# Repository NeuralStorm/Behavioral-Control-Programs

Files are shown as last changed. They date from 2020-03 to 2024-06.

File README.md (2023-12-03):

# Behavioral-Control-Programs

# Repo Layout

tilt_hardware_control/tilt_rewrite - tilt task control software  
tilt_hardware_control/tilt_docs - documentation for the tilt task hardware and software  
tilt_hardware_control/si_programmer_scripts - motor controller scripts for tilt task  
Primate_Joystick_Pull - NHP behavior task  
one_targ - center out task

## Related

schematics and board layouts for the voltage conversion board used with tilt_hardware_control are in the [hardware repo](https://github.com/NeuralStorm/hardware/tree/main/conversion_board)

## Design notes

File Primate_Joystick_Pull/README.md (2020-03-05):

# TempMonkeyImages
#EV01: Joystick 1 On
#EV02: Joystick 1 Off
#EV03: Joystick 2 On
#EV04: Joystick 2 Off
#EV05: Joystick 3 On
#EV06: Joystick 3 Off
#EV07: Joystick 4 On
#EV08: Joystick 4 Off
#EV09: Cineplex Home On
#EV10: Cineplex Home Off
#EV11: Cineplex Joystick On
#EV12: Cineplex Joystick Off
#EV19: Ready (Beginning of Trial)
#EV20: Correct Count (Time of Correct Tone)
#EV21: Incorrect Count (Time of Blooper Tone)
#EV23: Reward Count (Time of Reward)
#EV24: End of Trial
#EV25: DS 1
#EV26: GC 1
#EV27: DS 2
#EV28: GC 2
#EV29: DS 3
#EV30: GC 3
#EV31: DS 4 (Not Currently Used)
#EV32: GC 4 (Not Currently Used)

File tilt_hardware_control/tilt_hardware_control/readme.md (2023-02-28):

# Setup

Install dependencies  
`pip install -r requirements.txt`
`pip install -e ../../classifiers`

If using live graph view  
`pip install pyside6`  
if installation fails use  
`pip install pyside2==5.15.2`  

When using closed loop the plexon dll requires Visual C++ Redistributable for Visual Studio 2013  
https://www.microsoft.com/en-us/download/details.aspx?id=40784

# Usage

Example command line call
```bash
python main.py --config config.hjson
```

## Usage examples

Create a copy of `../tilt_docs/data_collection_template`.

`clock_source` will need to be changed to "internal" in `config.hjson` if running without the plexon system.

### Bias Collection

Run `run_bias.sh` in the data collection directory.

This will create a dated bias file.

### Open loop

Edit `config.hjson`; ensure `mode` is set to open_loop. Set `num_tilts` and `delay_range` to the desired values. `baseline`, `sham`, `reward` and `channels` can be ignored or removed from the config file.

Collect a bias file by running `run_bias.sh`.

Run `run_tilts.sh` in the data collection directory.  
This will read settings from `config.hjson` and create dated output files in the data collection directory.

The program will run through the specified number of tilts then wait for the user to press enter before exiting.

---
### Closed loop, initial run

Edit `config.hjson`; set `mode` to closed_loop, `baseline` to true and `sham` to false. Set `num_tilts`, `delay_range` and`reward` to the desired values.

Run `run_tilts.sh` in the data collection directory.  
This will read setting from `config.hjson` and create dated output files in the data collection directory.

The program will perform tilts and record the tilts and spikes.

---
### Closed loop, after initial run

Edit config used for the initial run and change `baseline` to false.  
Add `--template-in <file>` where `<file>` is the name of the template.json file created by the initial run.  
If a template file wasn't generated or different settings are needed a new template file can be generated using build_template.py.

Create or edit `labels.hjson`; set `channels` to the desired value. See [example_labels.hjson](./example_labels.hjson) for an example.

Run `run_tilts.sh` in the data collection directory.  
This will read settings from `config.hjson` and create dated output files in the data collection directory. Euclidian classifier templates are loaded from the specified template.json file.

The program will perform tilts and attempt to classify the tilt type based on the created templates and perform punish/reward actions based on if the classification was correct.

---
### Live view

Add the `--live` parameter to enable the live view.
```
python main.py --config config.hjson --monitor --live
```

### Calibrated live view

The path `/grf_python` will need to be substituted with the location of grf_python on your system ([Behavior-Analysis-Programs](https://github.com/moxon-lab-codebase/Behavior-Analysis-Programs), tested with commit `5f005e1a5530fd36f4ea0879e8453bc01a65871b`)

The environment variable `grf_python_path` must be set to the location of grf python.
e.g.  
`fish`
```
set -gx grf_python_path /grf_python
```
`bash`
```
export grf_python_path=/grf_python
```
`windows`
```
set grf_python_path=/grf_python
```

The python dependencies for grf_python will need to be installed.

Run the program
```
python main.py --config your_config.hjson --monitor --live-cal --live-bias ./your_bias_file
```

---
## Pausing

pressing enter will pause the program at the end of the current tilt. pressing enter will resume the program, pressing q then enter will exit the program

## Notes on clocks

Plexon outputs a 40khz clock signal. This is downsampled by a hardware downsampler to 1000hz and sent to Dev6/PFI6. Note that data collection must be started for the plexon system to output its 40khz clock.

Using plexon's clock signal instead of the internal nidaq clock means, given one known shared event (such as the start pulse), all the neural and grf data can be correlated in time. Without using a shared clock the two clocks will experience a different amount of drift and diverge over time.

clock_source should always be set to external in normal use.

## Strain guage reading recording

Strain guage data is recorded concurrently with the rest of the program.

Note: In some places the analysis pipeline refers to the side with two sensors as the hindlimbs but they could be the forelimbs if the animal is placed on the platform facing the other direction.  
With the forelimbs on a single sensor the sensor numbers correspond to the following limbs.  
sensor1: right hind limb  
sensor2: left hind limb  
sensor3: forelimbs

The output csv contains the following columns.

```
sensor1_s1
sensor1_s2
sensor1_s3
sensor1_s4
sensor1_s5
sensor1_s6
sensor2_s1
sensor2_s2
sensor2_s3
sensor2_s4
sensor2_s5
sensor2_s6
sensor3_s1
sensor3_s2
sensor3_s3
sensor3_s4
sensor3_s5
sensor3_s6
Strobe: signal that gos high when a tilt starts and low when it finishes
Start: ttl pulse indicating start of plexon recording
Inclinometer: Inclinometer
Timestamp: Timestamp (incremented by 1/sample rate for each row)
strobe_digital: digital version of Strobe passed through a schmidt trigger
tilt_midpoint: signal that gos high when the tilt reaches it's maximum inclination
stim: ttl pulse indicating stimulation was applied
```

# Program flow

The program has multiple modes, set with the `mode` config parameter. The behaviour of the different modes is listed below. Recording of analog data is handled the same way for all modes except bias (where live view can not be used). Stimulation works the same for all modes except bias and monitor where stimulation is not available.

## open_loop

```
create a list of tilt types
wait for start pulse
for i in 0..num_tilts:
    perform tilt i
    wait for after_tilt_delay
    if reward enabled:
        dispense water
    wait for a random time within delay_range
waits for the user to press enter
```

## closed_loop (baseline = true, yoked = false)

```
create a list of tilt types
wait for start pulse
for i in 0..num_tilts:
    clear pending plexon events
    start tilt i
    for event recieved from plexon within about 200ms:
        if event is a tilt:
            add event to classifier
        if event is a spike:
            add spike to classifier
    finish tilt
    wait for after_tilt_delay
    if reward enabled:
        dispense water
    wait for a random time within delay range
waits for the user to press enter
```

## closed_loop (baseline = false, yoked = false)

```
create a list of tilt types
for i in 0..num_tilts:
    clear pending plexon events
    start tilt i
    for event recieved from plexon within about 200ms:
        if event is a tilt:
            add event to classifier
        if event is a spike:
            add spike to classifier
    classify tilt
    if classification was correct:
        stop tilt and return to level
    if classification was incorrect:
        perform punish tilt
    finish tilt
    wait for after_tilt_delay
    if classification was correct and reward is enabled:
        dispense water
    wait for a random time within delay range
waits for the user to press enter
```

## closed_loop (baseline = false, yoked = true)

```
load list of tilt types from template
for i in 0..num_tilts:
    clear pending plexon events
    start tilt i
    wait about 200ms
    if recorded classification was correct:
        stop tilt and return to level
    if recorded classification was incorrect:
        perform punish tilt
    finish tilt
    wait for after_tilt_delay
    if recorded classification was correct and reward is enabled:
        dispense water
    wait for a random time within delay range
waits for the user to press enter
```

## stim

performs stimulation until enter is pressed

## monitor

waits for enter to be pressed (so recording/live view can be used without tilting)

## bias

records data for a fixed amount of time then exits

# Command line parameters

Some parameters aren't listed in the readme. Run the program with `--help` for a fill list of parameters.

`--config`  
path to hjson config file, see config parameters section

`--labels`  
path to labels config file, see label parameters section

`--bias`  
sets the mode to `bias`

`--overwrite`  
allows overwriting of existing output files

`--monitor`  
sets the mode to `monitor`

`--template-in`  
path to a template file created by a previous run of the program

required in closed loop non baseline, otherwise unused

`--template-out`  
automatically generate a template file at the specified path from the generated events and meta files before exiting

note: if there are a large number of spike events template generation could take a long time

`--loadcell-out`  
path to write ground reaction force data csv to

`--overwrite`  
overwrite exsting output files, if not specified the program will stop if the output file already exists

`--no-start-pulse`  
disable waiting for the plexon start pulse before performing tilts

`--live`  
show live graphs of analog recordings

# Config file

Config parameters that begin with `--` will be added to the passed command line parameters. Setting one of these paramaters to null will pass the command line parameter without a value following it.

The `-` parameter can be set to a list of strings which will be added to the command line parameters.

Other parameters are used as listed below.

## Config parameters

parameters marked with * are required in closed loop mode but do not need to be specified in other modes.  
parameters marked with ** are not required.  

`mode`: Literal['open_loop', 'closed_loop', 'monitor', 'bias']  
see program flow section

`clock_source`: Literal['external', 'internal']  
should normally be set to external

internal uses the internal nidaq clock. externel sets the clock to Dev6/PFI6

`clock_rate`: int  
The rate at which to collect samples in hertz.  
If clock_source is external this should typically be 1000.

`num_tilts`: int  
Number of tilts to perform. This number must be divisible by four. The tilts will be split evenly between the four tilt types.

`tilt_sequence`: Optional[List[str]]  
A fixed sequence of tilts to use instead of generating a randomized sequence. If specified `num_tilts` will be ignored. `sequence_repeat` and `sequence_shuffle` only apply if this parameter is specified.

`sequence_repeat`: int  
The number of times to repeat the tilt sequence.

`sequence_shuffle`: bool  
If true the tilt sequence is randomized. Applies before `sequence_repeat`.

`delay_range`: Tuple[float, float]  
Range of delays between trials in seconds.

`after_tilt_delay`: float  
Delay after tilt completion in seconds.

`baseline`*: Optional[bool]  
If false an input template will be used to classify tilts. If true spikes will be collected without performing classification.

`yoked`*: Optional[bool]  
If true the tilts from the input template will be repeated. If baseline is false the rewards and punish tilts will be repeated. `reward` must be true for rewards to be enabled.

`reward`: bool  
If true a water reward will be given after succesful decoding. If false no water reward will be given. If true the reward is always given with mode == open_loop or baseline == true.

`water_duration`: float  
Duration for which water is dispensed.

`plexon_lib`**: Optional[Literal['plex', 'opx']]  
'plex' uses the `pyplexclientts` library  
'opx' uses the `pyopxclient` library

'opx' should be used with newer plexon systems, 'plex' with older systems

defaults to 'opx'

`stim_enabled`: bool  

`stim_params`: Dict[str, Any]  

# Labels file

## Label parameters

`channels`: Dict[int, List[int]]  
Selects a set of plexon units to be used in the psth template. The parameters of the dict are plexon channels and the values are plexon units within that channel.

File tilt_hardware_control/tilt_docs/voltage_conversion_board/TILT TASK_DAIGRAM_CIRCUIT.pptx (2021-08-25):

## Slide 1

( Hardware Block diagram: Tilt system)

XS1/XS2 (Plexon Start)

TILT DAQ

Tilt type ( 8-bit Strobe-> DSP)

Plexon (MAP)

Spikes, evnts

Tilt type

Downsampler
clock

Motor Start (5)

TILT PC

1250 KHz clk

40KHz clk

Motor Start (24)

TTL conversion
cicrcuitry
(5<-> 24 V)

TILT SYSTEM
LOADCELL,
INCLINOMETER

PLEXON PC

SERVO DRIVE

Motor commands

Tilt type (5)

Spikes

(LFP, INC, ds clk)

SENSOR DATA

LOADCELL DAQ

Plexon (Breakout)

PREAMP

RAT

INC

LFP

For BMI:
Plexon PC can send Neural data to TILT PC via TCP/IP (PlexNet)

Tilt PC : Programs to send tilt events, BMI decoding, record load cell data

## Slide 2

NI-DAQ TO MOTOR

NOTE: YOU ALSO 2 MORE 5 TO 24 V CONVERTER , IF YOU HAVE TO PROVIDE BMI INTERRUPTS TO MOTOR

24V TO 5V (MOTOR START SIGNAL) START SIGNAL FROM MOTOR

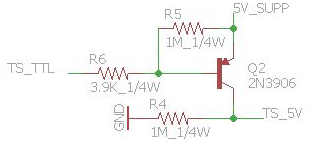
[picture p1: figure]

5 TO 12 V CONVERTER FOR WATER REWARD DELIVERY

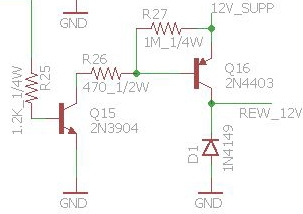
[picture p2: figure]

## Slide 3

Xcommon/ycommon/x7/x8-/x2-/x1- <->ground

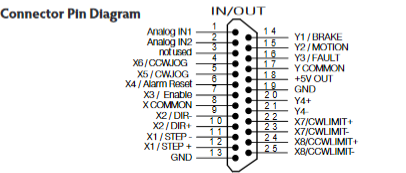
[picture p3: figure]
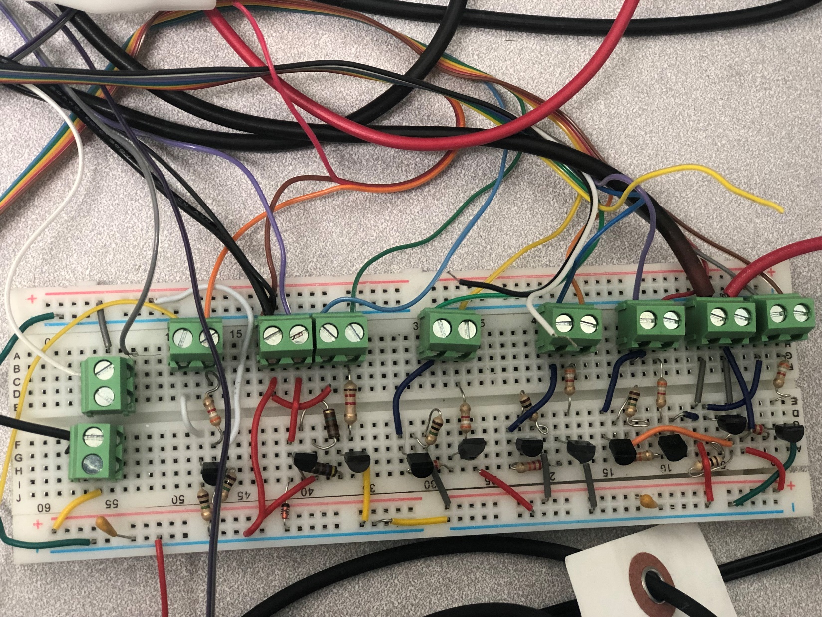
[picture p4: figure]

5 V SUPP

12V OUT PINCHER ( WATER)

GROUND

SMPS GROUND

GROUND

5 V LINE

24V SMPS SUPP

TTL_0 (IN->P0.0 NI6289 5V)

TTL_1 (IN->P0.01 NI6289 )

TTL_0 (O/P- MOTOR X3)

Y2 (MOTOR IN)

MOTOR OUT (TTL MOTOR START)

TTL_1 (O/P- MOTOR X4)

TTL_2 (IN->P0.2 NI6289 5V)

TTL_2 (O/P- MOTOR X5)

TTL_3 (IN->P0.3 NI6289 5V)

12 V LINE

TTL_3 (O/P- MOTOR X6)

12 V SUPP

WATER IN ( P0.4)

24V LINE

GROUND

GROUND

5 V INPUT FROM DAQ TO 24V OUTPUT (MOTOR)

24 TO 5V

5-12V WATER

X8+/x2+/ → bmi interrupt (punishment/reward)

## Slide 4

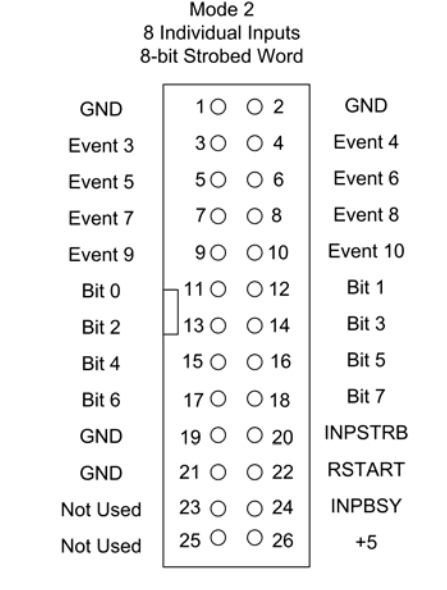
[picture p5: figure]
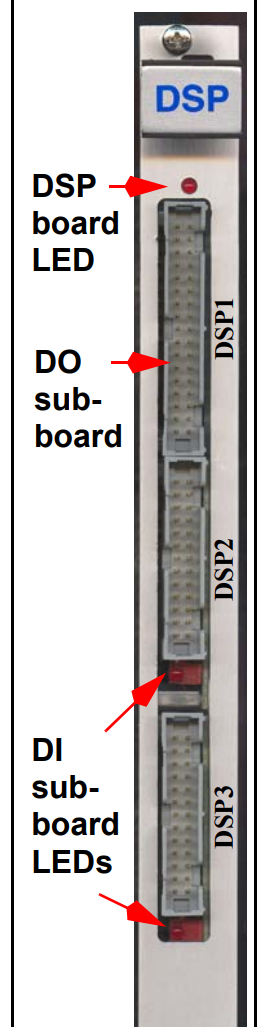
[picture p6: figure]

From TILT DAQ(USB 6289)

Motor start pulse

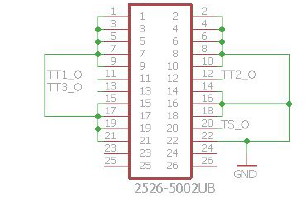
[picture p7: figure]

START PULSE FROM MAP ( XS1 TO NI DAQ 6289 P2.5)
INTERRUPT FOR BMI P1.2/P1.3 (USB 6289)

(MOTOR START)

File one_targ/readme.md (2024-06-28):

# Setup

copy `<project>/example_config.hjson` to `./config.hjson`

using python 3.11  
run `pip install .[hw]`

### Ubuntu 20 notes

To disable multi touch gestures in gnome the following extension can be installed.

https://extensions.gnome.org/extension/1140/disable-gestures/
```sh
gnome-extensions install disable-gestures@mattbell.com.au.v2.shell-extension.zip
gnome-extensions enable disable-gestures@mattbell.com.au
killall -3 gnome-shell
```

# Running

modify `./config.hjson` as needed

in bash
```sh
export nidaq=Dev3
export output_device=plexdo
one-targ
```

Press a to begin the task.

See comments in [example_config.hjson](./example_config.hjson) for descriptions of config parameters.

### Ubuntu 20 notes

If mouse input stops working after touch screen input `killall -3 gnome-shell` can resolve the issue.

# Hotkeys

\` (grave accent) - exit game  
`a` - start game  
`s` - stop game  
`f` - toggle fullscreen  
`c` - toggle calibration square (always 200x200 px)  

# Environment Variables

For environment variables marked [flag] any value that is set and not an empty string will enable the functionality.  
For example (bash)
```bash
export plexon=1
```

---
### `config_path`

use config file at path if no path is specified on the command line
default: `./config.hjson`

---
### `pos`

position the window with a specific location and size  
format {pos_x},{pos_y}<-{width}x{height}

this can be used to make the game effectively full screen

this changes how the game handles fullscreen and is likely required on ubuntu 20/gnome for correct functionality

example  
position at -1920,0
size 1920 by 1086
```sh
export pos='-1920,0<-1920x1086'
```

---
### `output_device`

juicer output device

`plexdo` - use plexon plexdo library  
`bridge` - use bridge  
`none` (default) - no output

---
### `nidaq`

nidaq device to use for event signal outputs. if not set nidaq output will be disabled

example
```sh
export nidaq=Dev3
```

---
### `bridge_enabled` [flag]

enables event output to the bridge server, enabled by default on linux  
if set to "`no`" bridge event output will be disabled

---
### `no_audio` [flag]

disables audio

---
### `photodiode_flash_duration`

photodiode marker flash duration in seconds, set to 0 to disable the photodiode marker flash  
default: 0.018

---
### `output_dir`

directory for output files  
default: `./output`

---
### `px_per_cm`

pixels per cm used to convert cm input values to pixels
default: 20.08

# misc dev notes

https://github.com/NeuralStorm/Behavioral-Control-Programs/tree/61a9baa6d198e3dc13d30326901ea78bd42dc77f/touchscreen_co/Touchscreen/One%20Targ

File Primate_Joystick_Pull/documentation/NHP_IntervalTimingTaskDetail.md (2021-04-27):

# Non-human Primate Interval Timing Task

## Homezone Exit task correct trial sequence

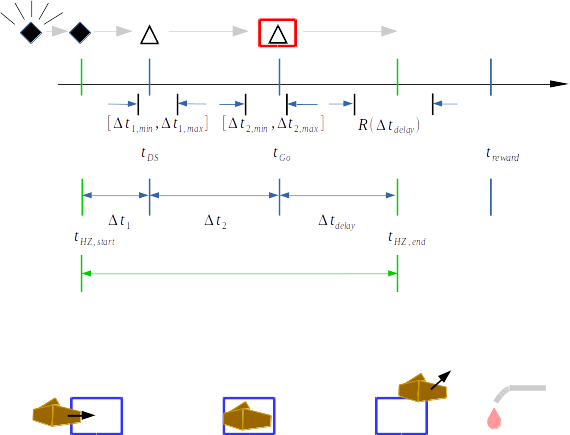
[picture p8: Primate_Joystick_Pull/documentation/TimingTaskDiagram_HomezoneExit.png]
NHP Homezone Exit task, correct trial sequence


Above: the series of animal-initiated events (green vertical markers), task-generated events  (blue vertical markers) and  measured intervals (horizontal arrows) during a correct trial of the homezone exit task.  The trial begins when on hand entry into the homezone target.  After a random interval of time between two user-specified limits $[\Delta t_{1, min}, \Delta t_{1, max}]$, a place-holder visual stimulus (triangle) is shown on the screen at $t_{DS}$.  The animal is cued to move its hand out of the homezone on appearance of a "Go" cue presented at $t_{Go}$; the Go cue takes the form of a red box that surrounds the discriminative stimulus already present on the screen.  If hand exit occurs within a user-specified limit a liquid reward is subsequently delivered, the volume of which scales as linearly-downward function dependent on $\Delta t_{delay}$.

Relevant parameters in `MonkeyImages_Joystick_Conf.py` as well as their corresponding key name and value(s) to load from configuration file, to setup "Homezone Exit" version of task:

- Version of task to run `TaskType`-> `Task Type`: `HomezoneExit` (ignored by program)
- Version of task to run `NumEvents`-> `Number of Events`: 0 (sets program to run homezone exit task)
- Graphics files directory path for task-specific visual stimuli: `source` -> `Path To Graphics Dir`: `"./TaskImages_HomezoneExit/"` (loads single triangle discriminative stimulus).
- ~~Number of unique intervals and relevant disciminative stimuli to setup in task: `NumEvents` -> `Number of Events`: `1`.~~
- `RewardClass(*Ranges)` -> `Ranges`: `1, 0.0, 3.0` (Function call to generate the single linear peak function for the sole discriminative stimulus (a triangle).  Description of each value in `Ranges` can be found in [Reward](#Reward) section below.)

## Joystick Pull Task correct trial sequence

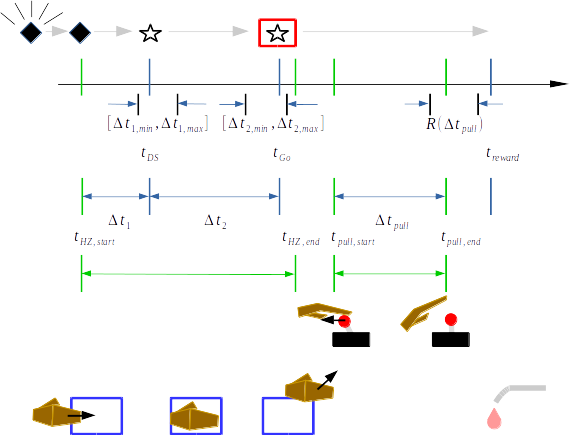
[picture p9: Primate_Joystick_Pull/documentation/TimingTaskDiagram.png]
NHP Joystick Pull task, correct trial sequence


Above: the series of animal-initiated events (green vertical markers), task-generated events  (blue vertical markers) and  measured intervals (horizontal arrows) during a correct trial of the interval timing task. After a random interval of time between two user-specified limits $[\Delta t_{1, min}, \Delta t_{1, max}]$, one of several possible discriminative stimuli is shown on the screen at $t_{DS}$; discriminative stimuli are geometric shapes that each code for a particular desired pull duration that the animal will be rewarded for producing later subsequently during the trial.  The animal is cued to start a joystick pull on the appearance of a "Go" cue presented at $t_{Go}$; the Go cue takes the form of a red box that surrounds the discriminative stimulus already present on the screen.  If the animal produces a joystick pull response of duration that falls within a user-specified time interval, a liquid reward is subsequently delivered, the volume of which scales as a bi-directional, linearly-dependent function of $\Delta t_{pull}$.

Relevant parameters in `MonkeyImages_Joystick_Conf.py` as well as their corresponding key name and value(s) to load from configuration file, to setup "Joystick" version of task:

- Version of task to run `TaskType`-> `Task Type`: `Joystick` (ignored by program)
- Graphics files directory path for task-specific visual stimuli: `source` -> `Path To Graphics Dir`: `"./TaskImages_Joystick/"` (loads three discriminative stimuli: oval, rectangle and star--one for each rewarded interval of the Joystick task.  More on this here [Visual Stimuli](#visual-stimuli)).
- Number of unique intervals and relevant disciminative stimuli to setup in task: `NumEvents` -> `Number of Events`: `3`. (sets the program to perform the joystick pull task)
- ~~`RewardClass(*Ranges)` -> `Ranges`: `3, 0.5, 0.25, 0.75, 0.5, 1.0, 0.75` (Function call to generate the three separate linear peak functions for the three discriminative stimuli in the joystick task.  Description of each value in `Ranges` can be found in [Reward configuration](#reward-configuration) section below.)~~
- `images` - see [the readme](../readme.md).
- `reward_thresholds` - see [the readme](../readme.md).

## Task Definitions (both versions)

### Negative Reinforcer type 1

When the animal's hand is outside of home-zone, a diamond shape flashes on screen at ~2Hz accompanied by and auditory ‘bell-dinging’ stimulus sounding repeating at ~0.5Hz.  These stimuli continue until animal’s hand enters home-zone.  This reinforcer is always present in both tasks; there is no boolean switch to turn it off.

Relevant parameters in `MonkeyImages_Joystick_Conf.py` as well as their corresponding key name and value(s) to load from configuration file:

- Graphics files directory link for visual stimuli -> `source` -> `Path To Graphics Dir`: `"./TaskImages_Joystick/"` or `"./TaskImages_HomezoneExit/"`.  Both contain the filled black diamond graphic that is to flash on the screen when the animal's hand is out of home zone.
- Audio file directory link (not included in config file) `OutOfHomeZoneSound` -> `'./TaskSounds/OutOfHomeZone.wav'`

### Task interval $\Delta t_1$ (task-generated)

The time interval spanning entry of hand into home-zone to appearance of the discriminative stimulus.  The duration of $\Delta t_1$ is randomly-drawn from a uniform distribution spanning $[\Delta t_{1,min}, \Delta t_{1,max}]$.  Animal must hold hand in home-zone for full duration of $\Delta t_1$ for the discriminative stimulus to appear.  If hand exits before the $\Delta t_1$ interval completes, the trial ends and the event is timestamped and recorded as a $t_1$-error.  Negative reinforcer type 1 immediately follows early exit occurrence to cue return of hand into home-zone if `EnablePullTimeOut == True`.

Relevant parameters in `MonkeyImages_Joystick_Conf.py` as well as their corresponding key name and value(s) to load from configuration file:

- $\Delta t_{1,min}$ -> `DiscrimStimMin` -> `Pre Discriminatory Stimulus Min delta t1`: `0.2` (seconds)
- $\Delta t_{1,max}$ -> `DiscrimStimMax` -> `Pre Discriminatory Stimulus Max delta t1`: `0.3` (seconds)
- $\Delta t_1$ -> `DiscrimStimDuration` -> Auto-generated in program from a uniform random draw in between limits above.

### Task interval $\Delta t_2$ (task-generated)

The time interval spanning appearance of the discriminative stimulus to appearance of the “Go” cue.  The duration of $\Delta t_2$ is randomly-drawn from a uniform distribution spanning $[\Delta t_{2,min}, \Delta t_{2,max}]$.  The "Go" cue is a red box that appears on screen that surrounds the (already present) discriminative stimulus.  The animal must continue to hold in home-zone for the full duration of $\Delta t_2$ for the Go cue to appear.  If animal's hand exits before interval completes, the trial ends and the event is timestamped and recorded as a $t_2$-error.  Negative reinforcer type 1 immediately follows early exit occurrence to cue return of hand into home-zone.

Relevant parameters in `MonkeyImages_Joystick_Conf.py` as well as their corresponding key name and value(s) to load from configuration file:

- $\Delta t_{2,min}$ -> `GoCueMin` -> `Pre Go Cue Min delta t2`: `0.45` (seconds)
- $\Delta t_{2,max}$ -> `GoCueMax` -> `Pre Go Cue Max delta t2`: `0.95` (seconds)
- $\Delta t_2$ -> `GoCueDuration` -> Auto-generated in program from a uniform random draw in between limits above.

### Negative reinforcer type 2

To follow post-go homezone exit events (Homezone Exit task) or pulls (Joystick task) of duration outside of the range associated with the discriminative stimulus.  Rewarded interval ranges are specified in `Ranges` parameter list as described in [Reward configuration](#reward-configuration).  In a negative reinforcement type 2 event, the screen goes dark for the duration `TimeOut`, with the option of an auditory "blooper" stimulus that sounds at the onset of the timeout period.

Relevant parameters in `MonkeyImages_Joystick_Conf.py`:

- `EarlyPullTimeOut` -> `Early Pull Time Out` : `FALSE` A Boolean switch for turning on/off occurrence of negative reinforcer type 2 to follow pull events that occur during either $\Delta t_1$ or $\Delta t_2$ intervals.  If `EarlyPullTimeOut` is set to `True`, the current trial ends on an early exit and negative reinforcer type 1 is presented.  If set to `False` the trial continues without interruption.
- `EnableTimeOut` -> `Enable Time Out`: `FALSE` A Boolean switch to enable type 2 negative reinforcement events to follow pull durations that are outside of rewarded range for the trial.
- `TimeOut` -> `Time Out`: `1.0` The duration of timeout intervals during type 2 negative reinforcement events in units of seconds.
- `EnableBlooperNoise` -> `Enable Blooper Noise`: `TRUE` A Boolean switch to specify if the "Blooper" sound should play at the start of type 2 timeout periods.
- `Bloop`: `'./TaskSounds/WrongHoldDuration.wav'` Audio file directory link (not included in config file) for blooper noise to be played on Negative Reinforcer type 2 events.

## Homezone Exit version trial sequence

After the appearance of the Go cue, the task monitors for disappearance of the hand marker from the home zone--a rectangular area in the top view of the reaching area of the rig as defined in Cineplex.  If disappearance does not occur within the time-ceiling of the rewarded interval as contained in `Ranges` ([Reward configuration](#reward-configuration) section), the trial ends, the lack of disappearance is recorded as a "no pull" event and the time of elapse is recorded after which a new trial begins following a time out period if enabed.  The time out occurs if `EnableTimeOut == True` that presents [negative reinforcement type 2](#negative-reinforcer-type-2).  If disappearance does occur (ideally in the form of removal of hand from home zone) within the time limit following Go cue appearance, the time of disappearance is measured as $\Delta t_{delay} = t_{HZ, end} - t_{Go}$ and a reward follows shortly thereafter.  The value of $\Delta t_{delay}$ determines the amount of fluid reward that is delivered to the animal as detailed in [Reward configuration](#reward-configuration).

Relevant parameters in `MonkeyImages_Joystick_Conf.py` as well as their corresponding key name and value(s) to load from configuration file:

- `NumEvents` -> `Number of Events`: `1`
- `RewardClass(*Ranges)` -> `Ranges`: `1, 0.0, 3.0` (seconds)
- `InterTrialTime` -> `Inter Trial Time`: `1.0` (seconds)
- `EnableTimeOut` -> `Enable Time Out`: `FALSE`
- `TimeOut` -> `Time Out`: `1.0` (seconds)
  
## Joystick Pull version trial sequence

Following Go cue presentation, task monitors for start of joystick pull.  If a pull does not occur within user specified amount of time (`MaxTimeAfterSound`) the trial ends, the absence of pull is recorded as a "no pull" event, the time of elapse is recorded and a new trial begins.  If pull occurs within time limit following Go cue appearance, the time of pull is measured as $\Delta t_{pull} = t_{pull,end} - t_{pull,start}$.  If $\Delta t_{pull}$ falls in the reward range associated with the particular discrimative stimulus on the screen, a fluid reward is delivered as described in [Reward configuration](#reward-configuration). If $\Delta t_{pull}$ is outside of the reward range for the trial, no reward is delivered, the trial ends, the times of the erroneous pull are recorded and classified as a "pull failure".  In the case of pull failure, if `EnableTimeOut == True`, then negative reinforcement type 2 is presented.  If `EnableTimeOut == False` the discriminative stimulus and Go cue remain on screen and the animal may attempt additional pulls for reward until the maximum time for the trial elapses (`MaxTimeAfterSound`).  Time-outs, if enabled, last for a duration specified by `TimeOut`  in units of seconds.  Successive trials are separated by an intertrial time of `InterTrialTime` in units of seconds.

Relevant parameters in `MonkeyImages_Joystick_Conf.py` as well as their corresponding key name and value(s) to load from configuration file:

- `MaxTimeAfterSound` -> `Maximum Time After Sound`: `20.0` (seconds)
- `InterTrialTime` -> `Inter Trial Time`: `1.0` (seconds)
- `EnableTimeOut` -> `Enable Time Out`: `FALSE`
- `TimeOut` -> `Time Out`: `1.0` (seconds)
  
## Reward configuration (outdated)

see `reward_thresholds` in [the readme](../readme.md) for updated information

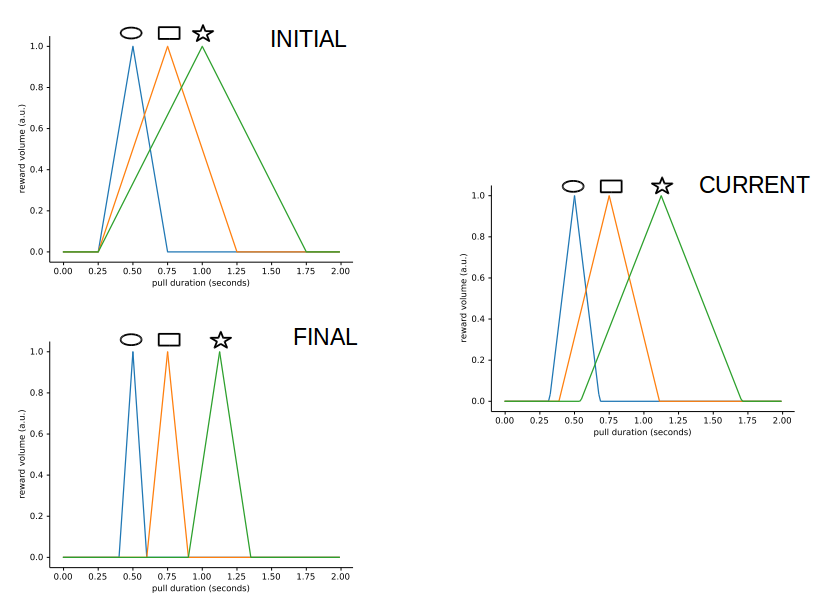
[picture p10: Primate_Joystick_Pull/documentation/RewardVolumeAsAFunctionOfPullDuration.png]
Reward volume as a function of $\Delta t_{pull}$


Functional relationship, depicted graphically, of fluid reward volume dependence on pull duration, $R(\Delta t_{pull})$, for each discriminative stimulus of joystick task.  Shown above each associated function peak is the corresponding Discriminative Stimulus (oval, rectangle and star) that is used to inform the desired pull duration for a given trial.  A triangle DS would appear over a single peak function for the case of the Homezone Exit version (not shown).  Peak values of functions are located at the desired pull duration (for the associated DS) for which a pull response elicits maximal reward.  Reward volume drops-off linearly the further away pull response duration departs from desired (location of peak) on a given trial.  Top Left: Reward function shapes at initial stage of training: the interval floors of disciminative stimulus-associated ranges are set at 0.25 seconds and functions have substantial overlap.  Bottom Left: End goal of reward functions after response shaping: DS-associated functions do not overlap.  Middle right: Current settings of DS-associated reward functions.

Relevant parameters in `MonkeyImages_Joystick_Conf.py` as well as their corresponding key name and value(s) to load from configuration file:

- `NumEvents` -> `Number of Events`: `1` or `3` (for Homezone Exit and Joystick tasks respectively)The number of disciminative stimulus-associated intervals to include in the task.
- `RewardClass(*Ranges)`: Method that generates each associated linear peak function for each discriminative stimulus to be included in the task.  In the argument list `Ranges`, the first in the list must be an integer number of intervals to include in the task.  This first argument is assigned to attribute `NumEvents` in the code.  Each group of two floats that follow in the `Ranges` list define the respective peak location $t_{peak}$, and peak width at base $\Delta t_{width}$ for each interval to be included.  Resulting peak function ($t_{floor} = t_{peak} - \Delta t_{width}$) and high boundary with respect to peak ($t_{ceiling} = t_{peak} + \Delta t_{width}$) for the associated interval.  That is, `RewardClass(*Ranges)` are of the form `Ranges` = $[N_{events}, t_{peak, 1},  \Delta t_{width,1}, ..., t_{peak, i}, \Delta t_{width, i}, ..., t_{peak, N}, \Delta t_{width, N}]$.  Examples: `RewardClass(3, 0.5, 0.25, 0.75, 0.5, 1, 0.75)` for Joystick task and `RewardClass(1, 0.0, 3.0)` for Homezone Exit version.
- `Ranges` is the key name in the configuration file that idetified the list of interval definition values (described above) that are read into the `RewardClass(*Ranges)` method.
- `MaxReward` -> `Maximum Reward Time`: `0.18` (seconds). Specifies the maxiumum time, in units of seconds, for which the feeder is advanced for all intervals--it corresponds to the peak height of each reward function.
- `RewardDelayMin` -> `Pre Reward Delay Min delta t3`: 0.5 (seconds).  Minimum length of delay before fluid reward delivery following completion of a successful trial.
- `RewardDelayMax` -> `Pre Reward Delay Max delta t3`: 0.5 (seconds).  Maximum length of delay before fluid reward delivery following completion of a successful trial.
- `RewardDelay = RandomDuration(RewardDelayMin, RewardDelayMax)`:  Method that draws actual length of delay separating reward delivery from trial completion on a particular trial.
- `UseMaximumRewardTime` -> `Use Maximum Reward Time`: `FALSE`.  Boolean toggle to override duration-dependent reward delivery $R(\Delta t_{pull})$ or $R(\Delta t_{delay})$. Instead, task simply delivers fixed-volume rewards of size `MaxReward` regardless of response accuracy.

Finally it is essential to note that each interval defined in `RewardClass(*Ranges)` must have corresponding graphics files of the associated discriminative stimulus and Go cue in the graphics file directory specified in the configuration file.  See [Visual stimuli configuration](#visual-stimuli-configuration).

## Visual stimuli configuration

In `MonkeyImages_Joystick_Conf.py` all visual stimuli are graphical files in Portable Network Graphic (.png) format.  Stimuli include the "enter homezone" cue (solid diamond), each of the discriminative stimuli (oval, rectangle and star shaped outlines) for the "Joystick" task and (triangle) for the "Homezone Exit" task as well as their corresponding images to cue reach (oval in red box, rectangle in red box and star in red box) and (triangle in red box)--the red box surrounding a DS is the "cue to start pull" or "Go" cue.  Stimuli also include the black blank screen presented during [Negative Reinforcement Events of Type 2](#negative-reinforcer-type-2).

Relevant parameters in `MonkeyImages_Joystick_Conf.py` as well as their corresponding key name and value(s) to load from configuration file:

- `source` -> `Path To Graphics Dir`: `"./TaskImages_HomezoneExit/"`or `"./TaskImages_Joystick/"`.  Path to folder containing all graphical image stimuli to be displayed during the course of a trial.  Files must be named alphabetically in order of their appearance in the trial sequence.
- `ChooseReward()` : Method to select, at random from a uniform distribution, the particular interval to be rewarded for the given trial, as well as the associated discriminative stimulus to present for the selected interval during the trial sequence.

## Task sounds configuration

Parameters to define auditory stimuli and cues given during task sequences for both "Joystick" and "Homezone Exit" versions of `MonkeyImages_Joystick_Conf.py`.  Relevant attributes and example values are as follows:

- `RewardSound = 'Exclamation'`.  Winsound used to indication successful completion of trial.
- `Bloop = str(Path('./TaskSounds/WrongHoldDuration.wav'))`.  Path to wav file of a "blooper" noise that is sounded (if enabled) at the onset of Negative Reinforcement type 2 event.
- `OutOfHomeZoneSound = str(Path('./TaskSounds/OutOfHomeZone.wav'))`.  Path to wav file of a "bell dinging" that is repetitively sounded at during Negative Reinforcement type 1 event (that signals for animal to return hand to home zone).
  
NOTE: The above parameter definitions are NOT included in the configuration file.  Alterations to sound file path parameters must be made to the code itself.

## Joystick channel selection (currently not implemented)

- `ActiveJoystickChans` -> `Active Joystick Channels`: `3`  Comma-separated list of channels to include for control of the Joystick Pull version of the task.  Value `3` corresponds to the "pull" direction of joystick (toward animal).  Channel `1` is the "push" direction (away from animal) and channels `2` and `4` are in directions of animal's left and right respectively.

## Unused (untested?) configuration options

These were included in early version of task development.  Not sure if functionality of these options has been tested.  Descriptions here are taken directly from comments in code.

- `ImageRatio`: `100` Example: ImageRatio = 75 => 75% Image Reward, 25% Water Reward , Currently does not handle the both choice for water and image. (Not included in configuration file)
- `WaterReward = self.WaterRewardThread()`: ??? (Not included in configuration file)
- `AdaptiveValue` -> `Adaptive Value`: Probably going to use this in the form of a value
- `AdaptiveAlgorithm` -> `Adaptive Algorithm`: 1: Percentage based change 2: mean, std, calculated shift of distribution (Don't move center?) 3: TBD Move center as well?
- `AdaptiveFrequency` -> `Adaptive Frequency`: Number of trials in-between calling `AdaptiveRewardThreshold()`

## Metadata and output filename generation

Meta data values record the who, what, when and why of a particular task session and include the values in the task output file for later classification.  Object attribute in code and corresponding key name in task configuration file are as follows:

- `StudyID` -> `Study ID` : 3 letter study code for the current task session (example value: `TIP`),
- `SessionID` -> `Session ID`:  Session type identifier code.
- `AnimalID` -> `Animal ID`: 3 digit animal identification number (example value: `001`).
- `Date` is auto-generated by the program at start up.
- `TaskType` -> `Task Type`:  (example values: `Joystick` or `HomezoneExit`)

When saving task events and performance statistics to an output csv file at the end of the session, the default filename for which is auto-generated as follows:

- `filename = StudyID + '_' + AnimalID + '_' + Date + '_' + TaskType + '.csv'`.
- Example: `TIP_001_20200715_HomezoneExit.csv`.

The file is saved to the destination path specified in the configuration file under the key:

- `savepath` -> `'Task Data Save Dir'` with the paired example value  `D:\IntervalTimingTaskData`.

## Task output

Pressing the "Save CSV" button on the task GUI during run-time generates a text file of task performance data in comma-separate value format.  The following list describes each field contained therein:

### Session level statistics

- `Total Trials`:  Total number of trials performed both successes and failures
- `Total t1 failures`:  Number of trials during which hand exited prior to DS-appearance
- `Total t2 failures`:  Number of trials during which hand exited prior to Go cue appearance
- `Total pull failures`:  Number of trials that animal pulled for a duration OUTSIDE of rewarded interval for the associated DS presented on a given trial.
- `No Pull`:  Number of trials for which the animal made no pull response after appearance of Go cue.
- `Total successes`:  Number of trials for which the animal made a pull response of duration within the rewarded interval for the associated DS presented on a given trial.
- `Check Trials`: `True` or `False`.  (I do not know what this field means...)
- `Paw into Home Box: Start`: For a given trial (indicated by column position) timestamp of hand entry into homezone.  Units of seconds since start of task.
- `Paw out of Home Box: End`  For a given trial (indicated by column position) timestamp of hand exit from homezone.  If trial outcome is a "no pull" then the end-of-trial timestamp is reported instead.  Units of seconds since start of task.
- `Discriminant Stimuli On`: For a given trial (indicated by column position) timestamp of first appearance of disciminative stimulus on the screen.   Units of seconds since start of task.
- `Go Cue On`: For a given trial (indicated by column position) timestamp of first appearance of Go cue on the screen.  Units of seconds since start of task.
- `Trial DS Type`: Identification number of desired pull duration interval and associated discriminative stimulus for the given trial.  ID number corresponds with order of intervals as they are listed in `Ranges` (in groups of two after the first argument) in the configuration file.  A value of `0` is reported if the trial ends in a $t_{1}$-error.
- `Duration in Home Zone`: Duration of time that hand is in homezone (seconds)--Calculated as `Paw out of Home Box: End` minus `Paw into Home Box: Start`.
- `Trial Outcome`: String-valued classification of trial outcome.  Possible values: (`'t1-Fail'`, - `'t2-Fail'`, `'Pull Fail'`, `'Success'`, `'No Pull'`).
- `Trial End`: Timestamp of trial completion regardless of outcome.  Units of seconds since start of task.
- `Post t1 failure pull counter`:  Number of pulls made by animal following occurence of $t_{1}$-error prior to start of next trial.
- `Post t2 failure pull counter`:  Number of pulls made by animal following occurence of $t_{2}$-error prior to start of next trial.

NOTE: For output files generated from HomezoneExit task sessions, hand exit events are listed as "pulls".

### Interval/DS-specific level statistics

- `Discriminatory Stimulus Trial Count #`: Number of intervals/DSs of type # during the session.
- `Correct Stim Count #`: Number of trials with success outcome for interval/DS type # subset.
- `Incorrect Stim Count #`: Number of trials with a fail outcome for interval/DS type # subset.
- `Correct Average #`: Average of correct response measure for interval/DS type # subset: $\bar{\Delta t_{pull}}$ for Joystick version and $\bar{\Delta t_{delay}}$ for Homezone Exit version.
- `Correct St Dev #`: Standard deviation of correct response measure for interval/DS type # subset.

### Interval/DS-specific event timestamps and durations

Timestamp of appearance or corresponding duration for each trial of interval/DS type # subset.  If event did not occur for trial due to error event, place-holder `------>` is inserted in cell that timestamp or duration would otherwise occupy.  One column per trial over course of the task session.

- `Discriminatory Stimulus #`
- `Go Cue #`
- `Correct Start Press #`
- `Correct End Press #`
- `Correct Duration #`
- `Reward Duration #`
- `Incorrect Start Press #`
- `Incorrect End Press #`
- `Incorrect Duration #`

## Task startup sequence

1. Turn power switch to "on" in back of OmniPlex Chassis
2. Turn on recording computer.
3. Start OmniPlex Server.  Configuration file 'TIP_Basic_2.pxs' should autoload.  Warning message appears; press OK.
4. Turn on PlexControl.  Load configuration 'TIP_Basic_NOSPK.pxc'.
5. Start Data Monitoring Mode ("Play" triangle icon in menu bar).
6. Check joystick real time output to verify proper connectivity.
7. Start CinePlex.  Load most recent (or desired) settings file.
8. Modify applicable configuration file (if necessary) in `C:\PythonSDK_python3\ConfigFiles`.
9. Start Anaconda Prompt.  Navigate to code directory `cd C:\PlexonSDK_python3\Behavioral-Control-Programs\Primate_Joystick_Pull`.
10. At the terminal command prompt, start virtual environment (python version 3.7, 32-bit) by typing `conda activate py37_32`.
11. Run the program by typing `python MonkeyImages_Joystick_Conf.py` at the command  prompt.  This should start the program and ask user to navigate and select applicable configuration file.
12. Select configuration file.  The terminal should next prompt user to start recording the PlexControl .plx file. Take this pause as an opportunity to arm CinePlex video recording if desired.
13. Start recording in PlexControl by pressing red triangular "play" icon.  A menu should appear asking for the save path and file name of the plx file to be written.  Enter in appropriate file name and destination path in navigator window.
14. The task window should now appear.  Drag window to rig monitor leaving "Start" button visible on the Plexon monitor screen for easy access.
15. Press "Start" button on task window to start task.
16. End task by pressing the "Stop" button on task window GUI.
17. Save task performance data by pressing "Save CSV" button on the task GUI.  Be sure to check terminal for successful save or a prompt to enter a unique filename.  The program should not save over file with same name unless instructed by user.
18. Remember to  end Plexon recording as well by pressing the square "stop" icon in top icon ribbon of PlexControl.

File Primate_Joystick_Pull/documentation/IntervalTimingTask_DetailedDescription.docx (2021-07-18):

Moxon NHP Lab – Joystick Task

Updated April 27, 2021 KM

The documents provides an overview of the training procedure for the joystick task and how the task is intended to progress. The goal of the training is to have the animals pull and hold a joystick for a specific temporal intervals depending on a cue.

Overview and Logistics

Training Phases

  1. Transporting
  2. Cage side joystick – encourage to hold for long time
  3. Painting hand
  4. Chair Training
  5. Head Restraints
  6. Hand in Home-Zone
  7. Go Cue
  8. Hold for Long duration
  9. Add second cue for shorter duration
  10. Add a third cue for additional duration
  11. Add a fourth cue

After monkeys have been chair trained and allow painting on their hand they will be trained to perform the Joystick task. In parallel, they are also being acclimated to head-restraining pads Task training will take place at least once per day, last no longer than 4 hours, Monday through Friday, in TB-144, room SS2016 of the CNPRC. Training is broken down into 9 Phases:

During training, the animal will be positioned in the chair and yoked with or without his head restrained, with the joystick within reaching distance of his extended forelimb. A reach-blocking plate on the chair will be used to permit reaching from either the monkey’s left or right side. The distance of the joystick from the chair will be positioned will be adjusted to accommodate different reach lengths of different monkeys. Monkeys may be trained to perform the task using limbs on either (or both) their left and/or right sides. Because neurons in motor cortex have been well documented to modulate their activation levels depending on the direction of reach (directional tuning) the animal will be required to start the task from a consistent (across trials) home position. Because motor preparation is also of interest, the animal will be required to wait for a go cue before initiating the joystick pull.

To guide the task, distinct auditory and visual cues will be presented. Visual cues are presented on flat-screen monitor within the monkey’s visual field. Auditory cues are played over speakers.

Definitions

Trial – a trial begins when the animal puts its paw in the home position. A trial ends when the animal either gets a reward or makes an incorrect response as defined below

Home position – the placement of the paw at the start of the trial where the marker on the animal’s paw is in the home zone

Home zone – a region defined by the Plexon video software. The software can monitor when the paw is in the home position by monitoring whether the marker on the back of the hand is in the home zone.

Task Parameters – parameters in blue are generated by the program, parameters in black are give by the user in the config file.

thome – the amount of time the animal must keep its paw in the home position for that trial. This number is a random variable, calculated by the program, selected from a uniform distribution between tmin and tmax

tmin – the minimal time the user wants the animal to keep its paw in the home position

tmax - the maximum time the user wants the animal to keep its paw in the home position

Δtlow Δthigh the precision with which the animal must hold his hand in home zone on each trial given by the user. For the Interval Cue Presentation step (see below) the animal must keep its paw in the home zone for at least thome - Δtlow. For the Reach Production step (see below) the animal must remove its paw from the home zone within thome + Δthigh

thpactual – the length of time the animal kept its paw in the home position, determined by the program

for intervals

number of intervals – the number of temporal intervals the program selects from to present as cues for the animal. Currently the number of intervals can be to 1, 2 or 3 to allow 1, 2 or 3 intervals. Or the number of intervals can be set to 0 and the program ends, giving the monkey a reward if he keeps his paw in the home position for thome

tpullmax and tpullmin – user defined minimums and maximums, define by the user for each interval, that the defines the range within which the monkey has to pull the joystick for a reward

e.g. tpullmin1 tpullmax1 tpullmin2 tpullmax2 tpullmin3 tpullmax3

tpull – the actual length of time the monkey pulled the joystick for – the joystick was in the activated state

trelease – the amount of time the program waits after the animal releases the joystick before a reward is delivered

Task progression

1. The monkey must have the marker on his responding hand positioned within the home zone to start a trial. This defines the start of a trial.

When a trial starts, the program randomly selects the cue from the user’s list of possible cues and calculates thome

2. Interval Cue presentation: Presentation of the interval occurs at the beginning of each trial as soon as the animal puts its paw in the home position. The particular cue presented (e.g. shape on the screen) indicates the duration of the joystick pull that will be rewarded.
3. Go cue: Animal must learn to hold its paw in the home position for the required period of time, from thome - Δtlow to thome + Δthigh. A correct response at this stage of the task is hand in home position the minimal amount of time thome - thome - Δtlow). An incorrect response at this stage is when the animal removes his hand from the home position early
  a. Correct Reponses -> program place a red circle around the interval cue (go cue) and continues to next step
  b. Incorrect response -> trial ends, blooper tone sounds, screen goes blank until monkey puts paw back into home position and then a new trial starts. Trial data are written to a file (trial number, tmin, tmax , thome, Δtlow Δthigh thpactual )
4. Reach production: The monkey must move its paw out of the home position within thome + Δthigh for a correct response. If the monkey leaves it paw in the home position for more than thome + Δthigh then it is an incorrect response
  a. Correct Reponses -> program continues to next step
  b. Incorrect response -> trial ends, blooper tone sounds, screen goes blank until monkey puts paw back into home position and then a new trial starts. Trial data are written to a file (trial number, tmin, tmax , thome, Δtlow Δthigh thpactual )

NOTE: if the number of intervals = 0, the program ends here. For a correct response the animal gets its reward and trial data are written to a file (trial number, tmin, tmax , thome, Δtlow Δthigh thpactual )

5. Interval production: The monkey must pull the joystick to the “on” position, keeping the mechanism in the activated state continuously for the cued duration. The cued duration is defined by the user as an interval between a max and min value, one set for each cue. An auditory tone sounds when the joystick is in on position (Hold Tone). On release, one of two cases will occur:
  a. Correct Response: The monkey releases the joystick within the specified time window about the target time between tmin and tmax for that interval. Program continues.
  b. Incorrect response: The monkey releases the button outside of the specified time window between tmin and tmax for the seleted interval. Trial ends, blooper tone sound, screen goes blank until monkey puts paw back into home zone and then new trial starts. Trial data are written to a file (trial number, tmin, tmax , thome, Δtlow Δthigh thpactual, interval number (1,2,or 3), tmin for that interval, tmax for that interval and tpull for the trial.)
6. Reward Event: An auditory tone sounds and a reward is delivered based on the pull interval (see below) trelease after the joystick is released. The trial is labelled a success, the trial ends and trial data are written to a file (trial number, tmin, tmax , thome, Δtlow Δthigh thpactual, interval number (1,2,or 3), tpullmin for that interval, tpullmax for that interval and tpull for the trial.)

Variants of this task are described in Knudsen,…,Moxon, J. Neurosci. 2014 and Zarco,…,Merchant J. Neurophys. 2009. Wang, …, Jazayeri, Nature Neuroscience

2018.

Auditory Stimuli

We plan to incorporate auditory stimuli into the to facilitate task acquisition and guide attention. Two or three distinct auditory stimuli--each comprised of a distinct pitch or timbre--would be generated from a nearby speaker at an intensity no louder than 80 decibels to signal:

1. During-hold: when the button or lever is in the activated (e.g. depressed or pulled) state.

2. Successful trial completion

3. Reward delivery

Visual Stimuli

A unique stimulus (computer graphics that can vary in terms of number shape and/or color) will code for each interval duration that a monkey must produce on a given trial to receive a reward. We plan on training at most six distinct interval-duration ranges, with corresponding visual stimuli, with values between 0.2 to 6 seconds.

Task acquisition

To train monkeys on the task, we will first gradually and imperceptibly increase the required duration that a monkey must keep paw in home zone to receive a reward. Once this is working well (what does ‘well’ mean). The reach to pull joystick for durations part of task will start.

Second, we will gradually increase the duration in order to receive reward until the max pull duration is achieved. Initially, the stimulus associated with the longest duration will be shown on the screen in front of the animal. Once the monkey regularly produces intervals of maximum duration (6 seconds), shorter duration trials, and their associated stimuli, will be introduced in a randomized sequence along with the long duration trials. Task acquisition will be evaluated statistically: that is, when an interval produced for the presented cue occurs at a frequency significantly greater than chance. If an animal reaches a max pull duration >2s but less than 6, a decision will be made to move on to a second duration.

Reward scaling

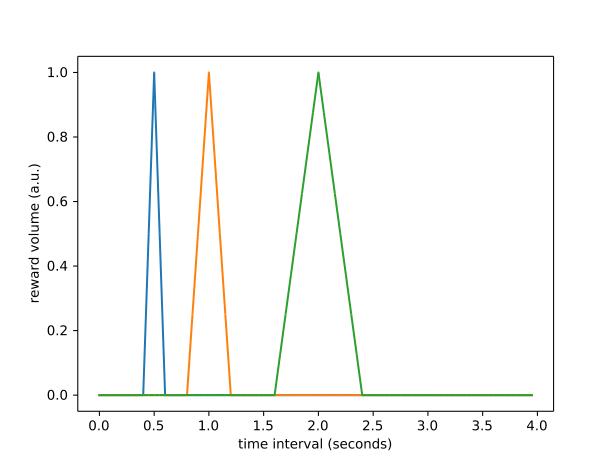
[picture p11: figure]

Figure 1: Reward volume as a function of produced interval. Target intervals in this example are located at the center of each peak at 0.5, 1.0 and 2.0 seconds. Widths of peaks increase linearly with duration of target interval.

Because production of long intervals requires more effort and attention than short intervals, we could have monkeys receive greater reward (e.g. greater volume of applesauce) for successful completion of long intervals. Volume of sauce reward will scale with duration of the produced interval. This follows methods described in Zarco, …, Merchant J. Neurophys 2009.

Alternatively, amount of reward could also be delivered as a multi-peak function emphasizing interval precision; that is, with each peak located at the location of each target interval to be produced and with peaks about longer target intervals having greater width. See figure 1. below illustrating hypothetical reward volume as a function of produced interval according to this paradigm. A similar reward paradigm is described in Wang, …, Jazayeri, Nature Neuroscience 2018.

Weber’s Law

We expect variability of timed interval responses from monkeys to observe Weber’s law: standard deviation of the distribution of produced intervals is directly proportional to the average duration of those intervals. Therefore, rewarded ranges about long target intervals will be set comparatively wider than rewarded ranges for shorter target intervals (e.g. if the range of rewarded intervals about target interval t = 0.5 is [0.4, 0.6], the rewarded range about target interval t = 1.5 might be [1.25, 1.75]).

Performance shaping – this did not work well for us

~~Once task acquisition has been demonstrated, press durations will be further shaped by gradually and imperceptibly reducing the range of durations that are rewarded about the target duration. For example, for a desired press duration of t = 2 seconds, the range of rewarded press durations on these trials will be gradually reduced from between 1 to 3 seconds to 1.5 to 2.5 seconds. Range limits will be adjusted in increments of +or-~~ ~~0.05~~ ~~sec for every~~ ~~100~~ ~~trials completed.~~

~~To maximize the number of presses made by monkeys during training, and subsequent testing, the ratio of number of correct presses to number of rewards will be gradually and imperceptibly increased under a variable reinforcement schedule. Specifically, the reward ratio will be increased by~~ ~~0.01~~ ~~for every~~ ~~200~~ ~~correct trials completed, starting at 1:1 until the reaching a possible maximum of~~ ~~6:1~~~~. The end goal of SPHT training is for a monkey to perform a series of presses, ranging between~~ ~~0.2 to 6~~ ~~seconds for no less than~~ ~~200~~ ~~trials per session.~~

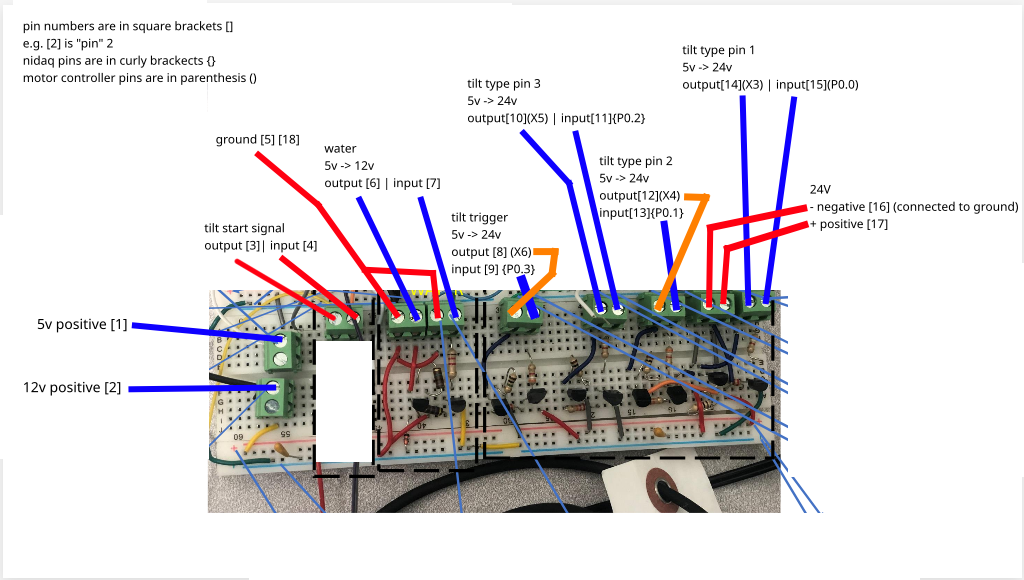
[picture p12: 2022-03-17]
tilt_hardware_control/tilt_docs/voltage_conversion_board/voltage_conversion_board_pinout.png

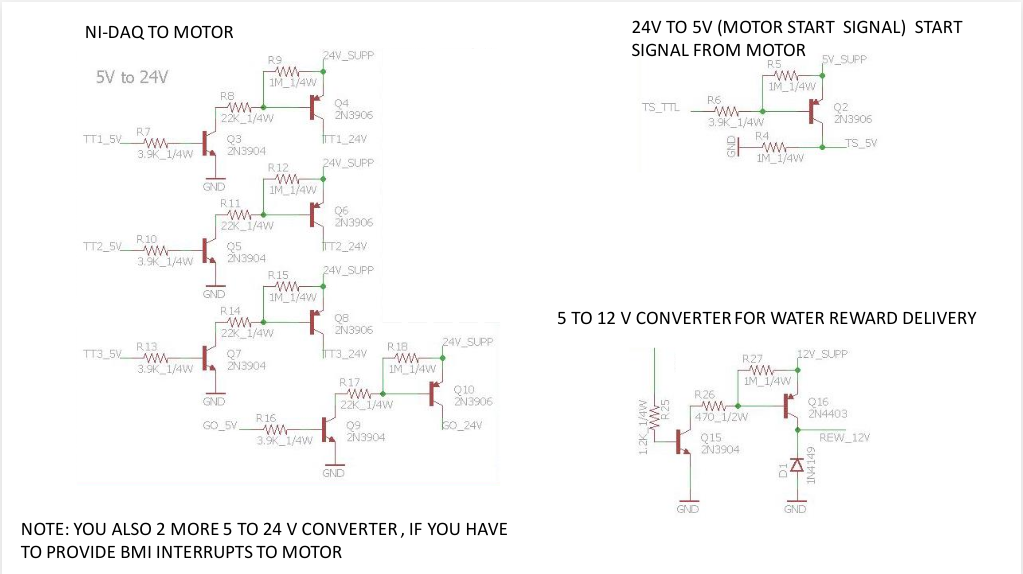
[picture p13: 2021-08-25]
tilt_hardware_control/tilt_docs/voltage_conversion_board/shot_20210824_215824.png

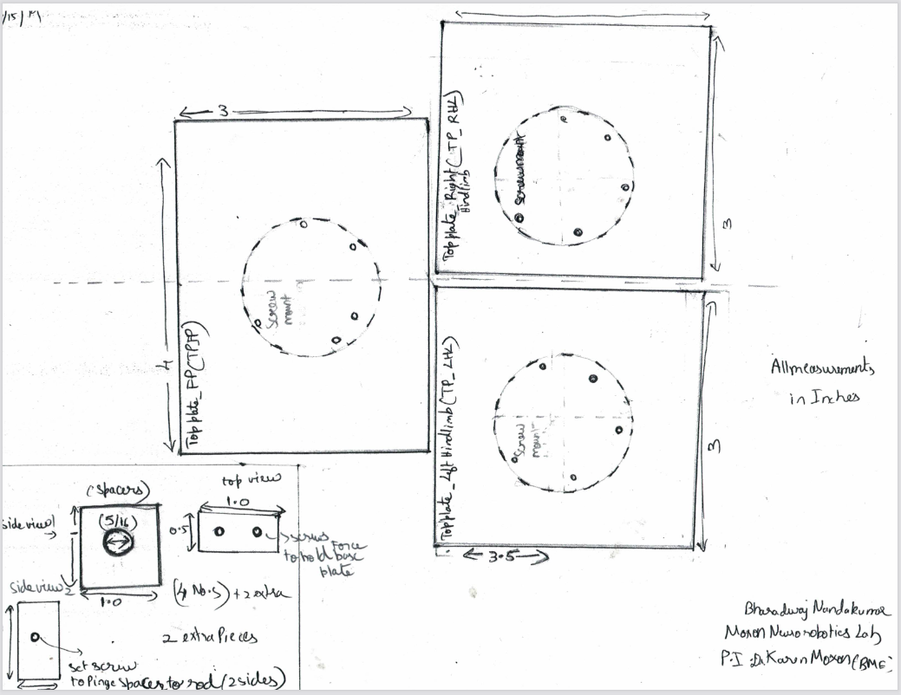
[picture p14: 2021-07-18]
tilt_hardware_control/tilt_docs/platform_drawing_top.png

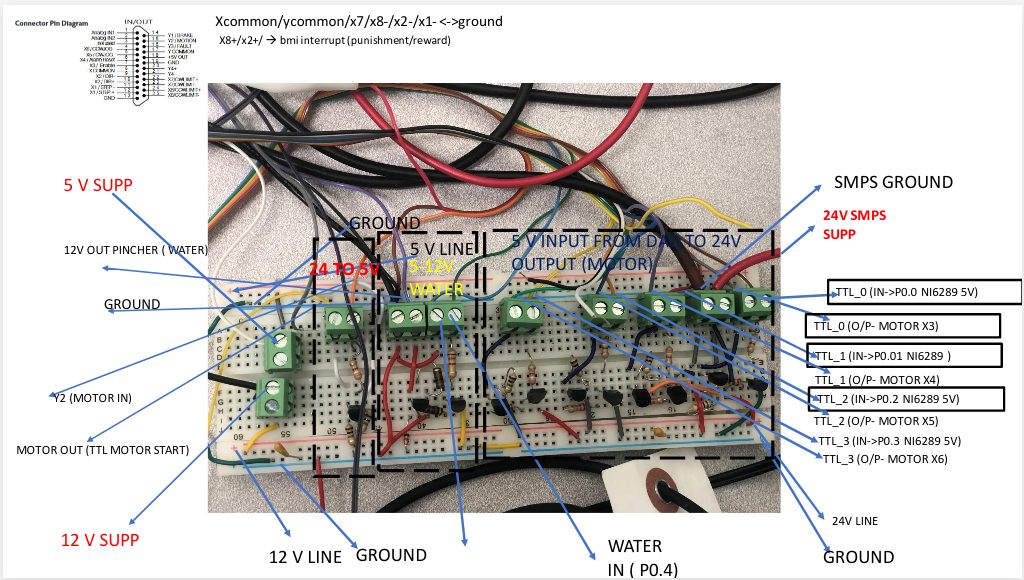
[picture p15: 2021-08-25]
tilt_hardware_control/tilt_docs/voltage_conversion_board/shot_20210824_215838.png

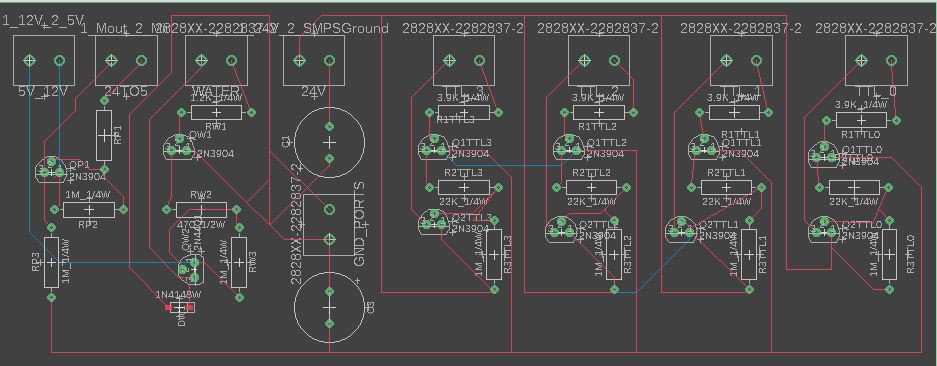
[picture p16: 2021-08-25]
tilt_hardware_control/tilt_docs/voltage_conversion_board/CircuitImage.JPG

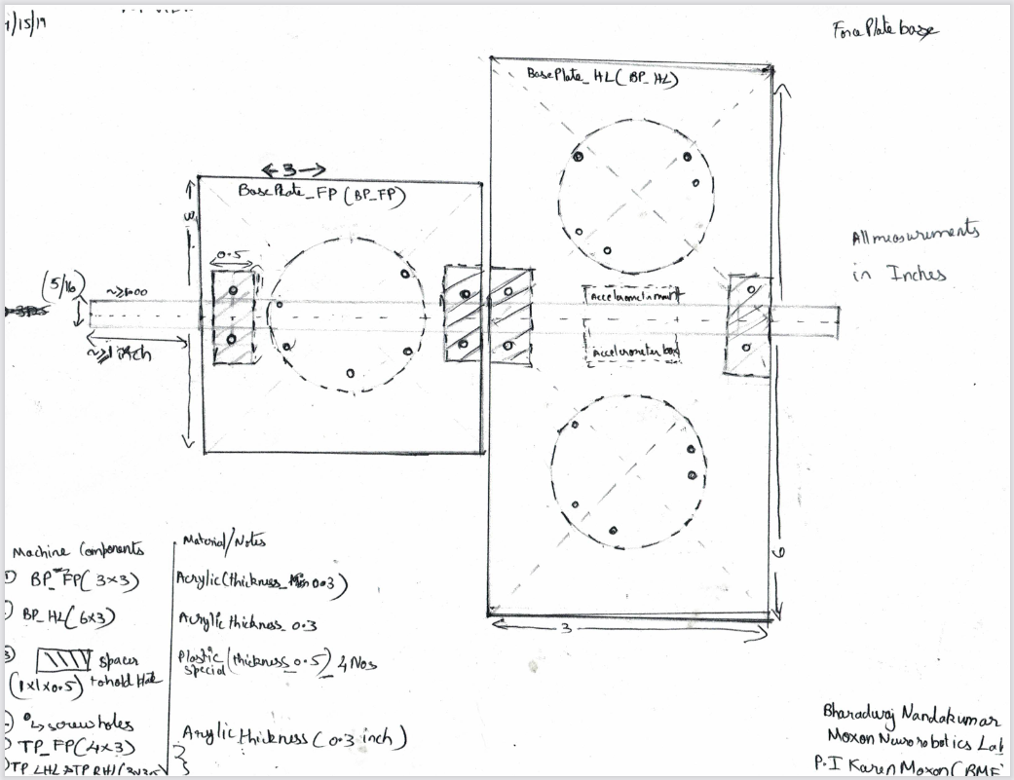
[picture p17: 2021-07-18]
tilt_hardware_control/tilt_docs/platform_drawing_bottom.png

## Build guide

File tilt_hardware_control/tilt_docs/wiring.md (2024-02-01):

for devices besides the voltage conversion board the pinouts can be found in the manual for the given device. note that for the for the USB pinout information is in the SCB-68 quick reference for the SCSI version

the force/toque sensors connect to the nidaq directly via a scsi connector. the SCB-68 breakout board is daisy chained through the sensor amplifier  
"CONNECTOR 0" on the nidaq connects to "Connector 0 to DAQ Card" on the amplifier  
"CONNECTOR 1" on the nidaq connects to "Connector 1 to DAQ Card" on the amplifier  
"Connector 1 from User" connects to the SCB-68 breakout board

## devices

pin numbers are prefixed based on the device/port, e.g. tim(5) is pin 5 on the plexon timing board

---
`downsample` - clock downsampling board

port numbers correspond to the labels on the downsampling board

---
`nidaq` - SCB-68 breakout board on conenctor 0 of the NI 6225 nidaq connected to the tilt computer

port numbers will have both the number labeled on the breakout board and the pin's name  
e.g. `nidaq(P0.0|52)` is pin P0.0 and labeled 52 on the SCB-68 breakout board

in cases where pins have multiple functions only the relevent one will be written, e.g. `PFI 6 / P1.6` will be listed as `PFI 6`

---
`motor` - SV7-Si motor controller IN/OUT1

port numbers will have both the port number and part or all of the name, e.g. `motor(Y2|15)` is port 15 which has the name "Y2 / MOTION"

the SI software refers to pins Y1-Y4 as output 1-4, X1-X4 as input 1-4. these terms may be used interchangably in some places

---
`tim` - plexon TIM board d-sub connector

port numbers will have both the port number and the name, e.g. `tim(40 kHz|5)` is port 5 which is named "40 kHz"

---
`din` - plexon DIN board port B

port numbers will have both the port number and part or all of the name, e.g. `din(Data 1|17)` is port 1 which has the name "Data 17"

---
---

## ground
the following pins should all be connected together

`nidaq(AI GND|67)`  
`nidaq(D GND|12)`  
`conv(5)`  
`conv(18)` (optional)  
`conv(16)` (optional)  
`downsample(Pwr -)`  
`downsample(In -)`  
`downsample(out -)`  
`din(Ground|19)`  
`tim(GND|15)`

## power
the nidaq, plexon, f/t sensor amp and motor controller have external power sources that need to be connected

`downsample(Pwr +)` - `nidaq(+5V|8)`

## tilt type to plexon

`nidaq(P2.2)` - `din(Data 22|6)`  
`nidaq(P2.3)` - `din(Data 25|9)`  
`nidaq(P2.4)` - `din(Data 21|5)`  
`nidaq(P2.5)` - `din(Data 24|8)`

## tilt timing for recording

`nidaq(P2.0)` - `nidaq(P0.0)`  
`nidaq(P2.1)` - `nidaq(P0.1)`

## inclinometer

the inclinometer should be connected to `nidaq(AI 10|31)`

## plexon clock

`tim(40 kHz|5)` - `downsample(In +)`  
`downsample(out +)` - `nidaq(PFI 6|5)`

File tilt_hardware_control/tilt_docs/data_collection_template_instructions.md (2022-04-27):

create a copy of the `data_collection_template` directory, the copy should go somewhere outside the `tilt_hardware_control` directory  
the template directory can be found in the tilt_docs directory which is pinned to Quick Access

modify `config.hjson`

`.sh` files can be run in git bash by double clicking them

`run_tilts.sh` performs tilts and collects data from the grf sensors, displays the live graphs  
`run_bias.sh` collects a bias file  
`run_monitor.sh` displays the live graphs and collects data without tilting

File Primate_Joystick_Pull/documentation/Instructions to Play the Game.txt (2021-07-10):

Start Omniplex server
Open PlexControl – load config file (be sure the system is stopped – black square with green line)

Open Cineplex – load config file joystick task.txt
Arm the video – hit the white A in the red circle

Go to:
C:\PlexonSDK_python3\Behavioral-Control-Programs\Primate_Joystick_Pull
Right click in Explorer – select ‘Gitbash Here’
In the command window type:
winpty py MonkeyImages_Joystick_Conf.py
Opens file selection dialogue.Open file:
 C:\PlexonSDK_python3\Behavioral-Control-Programs\Primate_Joystick_Pull\csvconfig_EXAMPLE_Joystick.csv
Start Plexon Recording (hit the start record icon)
 Select a file to write data to

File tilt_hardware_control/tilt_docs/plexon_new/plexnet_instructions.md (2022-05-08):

plexon: 128.120.197.198
tilt  : 128.120.197.189

Below my email signature, I've included some information for getting PlexNet set up. When you refer to the below ideas (in the steps below my email signature), please note that the “PlexNetLocal.exe”, “PlexNetRemote.exe”, and “PlexClient.dll” all come bundled with the installation of the specific version of the OmniPlex software which the customer is using. These files can be found at “C-->Program Files (x86) -->Plexon Inc-->OmniPlex”. Please be sure to use these specific versions of these files when considering the below ideas.

Quick Start for PlexNet:

1) Start OmniPlex and begin data acquisition normally.
2) Run PlexNetLocal.exe
3) Write down the IP address shown in PlexNetLocal.
4) Copy PlexNetRemote.exe and PlexClient.dll to the remote PC.
5) On the remote PC, run PlexNetRemote.exe.
6) In PlexNetRemote, click “PlexNet Server Address and Port.”
7) Enter the IP address that you wrote down in step 3 (from PlexNetLocal).
8) Click OK.
9) Click “Connect.”
10)You should see messages indicating that PlexNetRemote is connected and that data is being received.
a. The MMF bar populating/updating indicates that data’s flowing. Also, a non-zero “kb/s” value indicates that data is flowing.
11) At this point, you can run an online client on the remote machine, which will receive data just as if it were running on the same PC as OmniPlex.  
a. In PlexNetRemote, the “Data Transfer Options” allow you to configure things like which continuous channels are sent over PlexNet. Most clients don’t need things like the wideband continuous data, so by default those channels are not sent over PlexNet. Note that you have to click “Connect” before PlexNetRemote will let you see the Data Transfer Options.  
If you’re interested in WB and/or SPKC data getting to PlexNet Remote, you also have to go to OmniPlex Server and do these steps:
    1. Stop Data acquisition.
    2. Click Online Client Options. [ConfigureOnline Client Options]
    3. Set the sampling rate to 40,000 Hz. (default is 1000).
    4. Make sure “Enable Online Client access…” is checked.
12) When you are done running clients on the remote machine, click Disconnect in PlexNetRemote.

After this first-time setup, just perform steps 1,2,5,9 to start, and 11,12 to shut down. You don’t need to re-enter the IP address in PlexNetRemote, unless the IP address of the local PC changes. To keep things simple, on the remote machine place PlexNetRemote.exe and PlexClient.dll in the same folder as your client programs. This avoids issues with the client not being able to find PlexClient.dll, or finding the wrong version.

Some settings that should generally not need to be changed:
If for some reason the default of port 6000 is not acceptable, for example, the network administrator has blocked or reserved it, find out what port number is available and enter that value in both PlexNetLocal and PlexNetRemote.

Leave the protocol set to the default of TCP/IP in both Local and Remote. Only change this setting to UDP if the remote machine does not support TCP/IP, which is rare.

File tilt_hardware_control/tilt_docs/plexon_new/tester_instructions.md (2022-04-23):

parts:  
* the blue rectangular piece called the DI Status indicator
* the small green piece called the DI Generator

# Usage

For your testing, please go into the OmniPlex Server software and set Port A to “Event Word” Mode and set Port B to “Individual Events” mode. Please set the logic to High True for both ports for the testing. Chapter 10 of the OmniPlex User Guide https://plexon.com/wp-content/uploads/2020/01/OmniPlex-User-Guide.pdf provides useful information for setting up this configuration.

The first thing you can try is simply plugging in the DI Status indicator piece (the blue rectangular piece) first into Port A, and then next into Port B. When you do this, is every light on the DI Status Indicator illuminating in each case? This would be expected behavior if so. If this does not happen, please let us know. The behavior for LEDs “A”, “B”, and “C” is not strictly defined,  so if you see different behavior for those three LEDs specifically, that is not problematic.

After verifying the above, then next please plug the DI Status Indicator piece back into Port A. Then, plug the DI Generator (the small green item) into the other end of the DI Status Indicator. When the DI Generator is plugged in, it receives power from the Digital Input card, and this causes the DI Generator to generate a pattern of digital signals. When the DI Generator is plugged to the Digital Input card, it repeats the following pattern:

It raises bit 0, then raises and lowers the STROBE bit, then it lowers bit 0. For each of the remaining output bits (1 to 15), the generator continues this pattern. It raises the bit, raises and lowers the STROBE bit, and then lowers the bit. Finally, after bit 15 has been lowered, the DI generator raises and lowers the RSTART bit.

When  you run through this process with the DI Generator plugged into Port A (Event Word mode), the raising of the STROBE bit generates a strobed event in OmniPlex. The strobed event has a value associated with it corresponding to the setting of the individual bits at the time the STROBE was raised. Sine the DI generator raises one bit at a time, 16 strobed event values are generated (1,2,4,8…32768).

When you run through this process with the DI Generator plugged into Port B (Individual Events mode), the raising of a single bit generates a corresponding event in PlexControl software. Bit 0 creates an event 1 (EVT17 since port B corresponds to EVT17-EVT32), bit 1 creates EVT18, etc. In this mode, raising the STROBE bit does not generate any events.

In either of the test modes mentioned above, the rising of the RSTART bit generates an RSTART event and the lowering of the RSTART bit creates an RSTOP event. Note however that only Port A on the Digital Input card generates RSTART and RSTOP events.

If you’d like you can make one short (~10-20 second) PL2 file recording for each of the Ports using the above testing set-up described for each port, and you can send us these short recordings, so that we can look at the recordings in the NeuroExplorer software.

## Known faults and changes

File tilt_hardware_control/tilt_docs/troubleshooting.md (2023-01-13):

# Common errors

`daqmx.errors.DaqError: Some or all of the samples requested have not yet been acquired.`

This is typically caused by plexon data acquisition not being started. The plexon system only generates the needed clock signal while data acquisition is running.

If neural data is not being collected the clock source can be switched to internal.

---

`daqmx.errors.DaqError: The specified resource is reserved. The operation could not be completed as specified.`

Ensure no other instances of the tilt control program is running, including in monitor mode. If this doesn't work the python processes may need to be killed with task manager.

The device can be made available by resseting it in NI Max but this can leave left over processes that can still interact with other shared resources so it is likely better to restart the computer.

This can also be resolved by restarting the computer.

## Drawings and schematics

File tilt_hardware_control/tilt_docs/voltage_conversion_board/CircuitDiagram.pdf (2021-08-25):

# 2N3904 GND

# 2 TTL_0

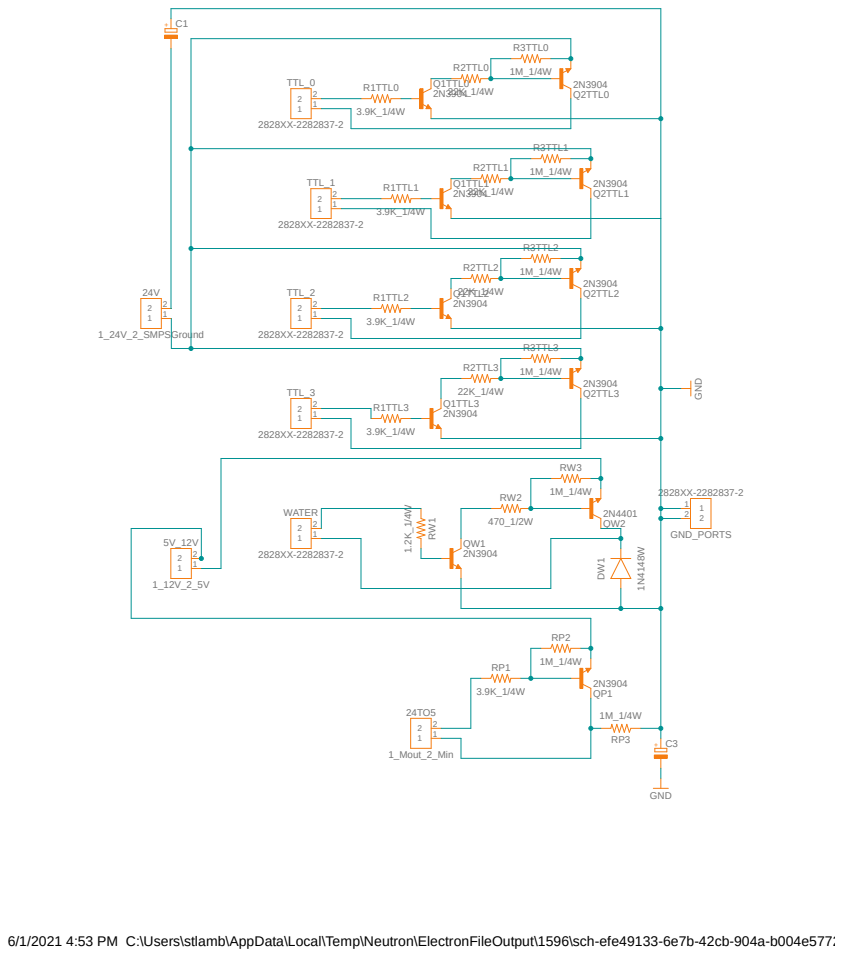
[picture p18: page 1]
GND ¹.2K_1/4W; 1_Mout_2_Min; 2 RW¹; QW2 DW¹; 1N⁴¹⁴⁸W; R1TTL3; R2TTL3; R3TTL3; Q1TTL3; Q2TTL3; R1TTL2; R2TTL2; R3TTL2; Q1TTL2; Q2TTL2; R1TTL1; R2TTL1; R3TTL1; Q1TTL1; Q2TTL1; R1TTL0; R2TTL0; R3TTL0; Q1TTL0; Q2TTL0; TTL_3; 2 TTL_2; 2TTL_1; 1_24V_2_SMPSGround; 2 WATER; 2 GND_PORTS

6/1/2021 4:53 PM C:\Users\stlamb\AppData\Local\Temp\Neutron\ElectronFileOutput\1596\sch-efe49133-6e7b-42cb-904a-b004e5772f45\MoxonCircuitBoard v7.sch (Sheet: 1/1)

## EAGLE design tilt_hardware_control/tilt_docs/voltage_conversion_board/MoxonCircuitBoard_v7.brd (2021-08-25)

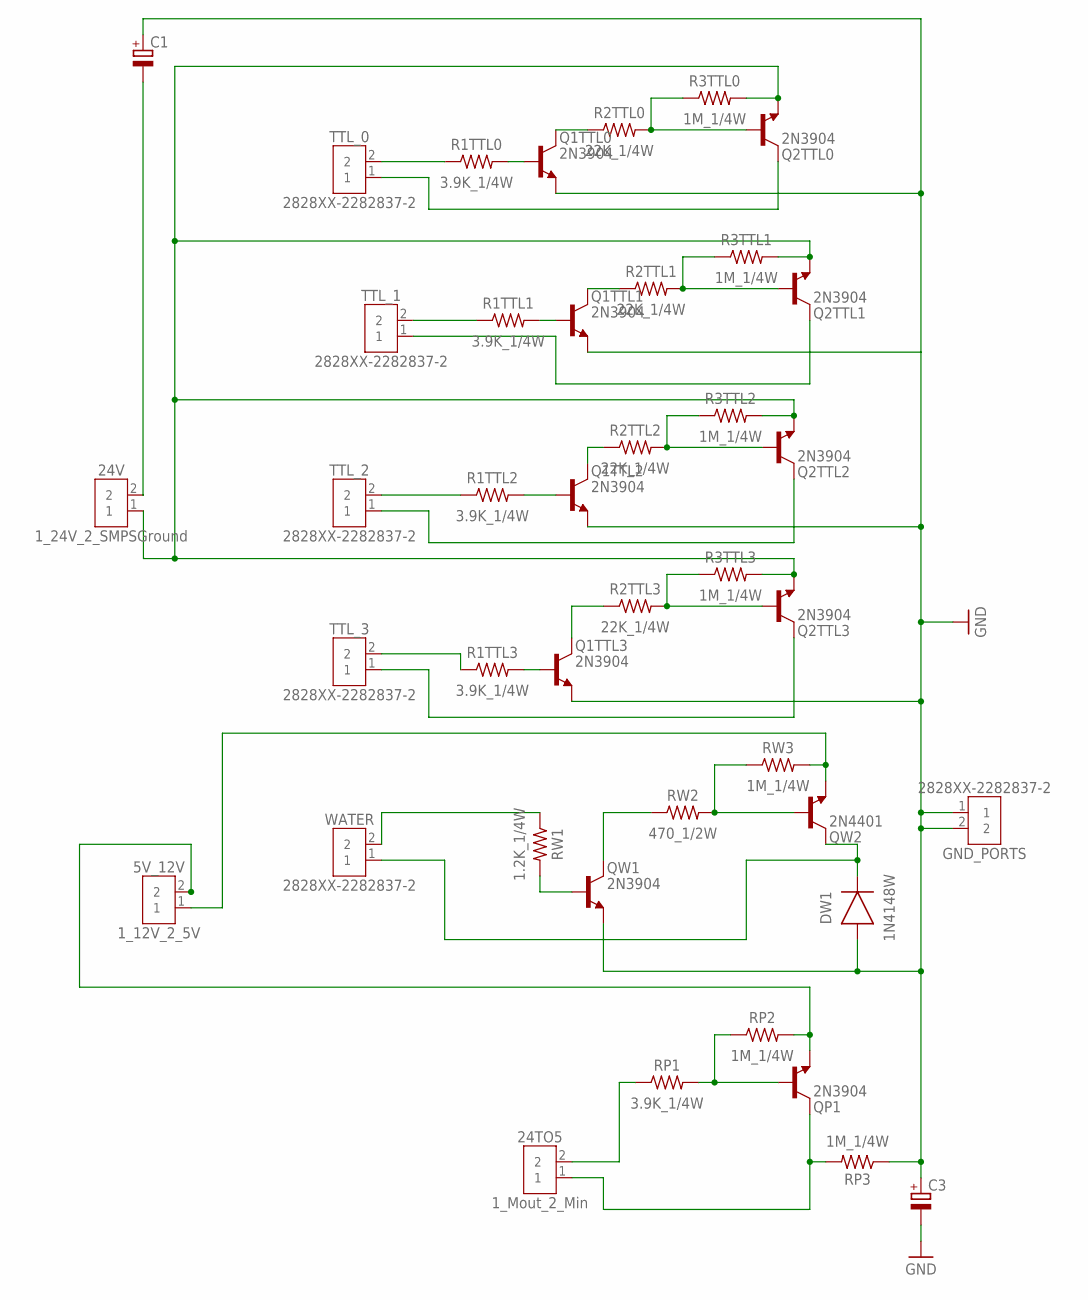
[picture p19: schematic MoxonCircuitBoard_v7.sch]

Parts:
5V_12V: 1_12V_2_5V; TERMBLK_508-2N
24TO5: 1_Mout_2_Min; TERMBLK_508-2N
24V: 1_24V_2_SMPSGround; TERMBLK_508-2N
C1, C3: C-POL_RADIAL-20MM-DIA; CAPPRD550W60D1200H2000B
DW1: 1N4148W; SOD3715X135
GND_PORTS: 2828XX-2282837-2; TERMBLK_508-2N
Q1TTL0, Q1TTL1, Q1TTL2, Q1TTL3, Q2TTL0, Q2TTL1, Q2TTL2, Q2TTL3: 2N3904; TO92
QP1: 2N3904; TO92
QW1: 2N3904; TO92
QW2: 2N4401; TO92
R1TTL0, R1TTL1, R1TTL2, R1TTL3: 3.9K_1/4W; RESAD1176W63L850D250B
R2TTL0, R2TTL1, R2TTL2, R2TTL3: 22K_1/4W; RESAD1176W63L850D250B
R3TTL0, R3TTL1, R3TTL2, R3TTL3: 1M_1/4W; RESAD1176W63L850D250B
RP1: 3.9K_1/4W; RESAD1176W63L850D250B
RP2, RP3: 1M_1/4W; RESAD1176W63L850D250B
RW1: 1.2K_1/4W; RESAD1176W63L850D250B
RW2: 470_1/2W; RESAD1176W63L850D250B
RW3: 1M_1/4W; RESAD1176W63L850D250B
TTL_0, TTL_1, TTL_2, TTL_3: 2828XX-2282837-2; TERMBLK_508-2N
WATER: 2828XX-2282837-2; TERMBLK_508-2N

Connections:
GND: C1.1 (+), C3.1 (+), C3.2 (-), DW1.2 (A), GND_PORTS.1, GND_PORTS.2, Q1TTL0.1 (E), Q1TTL1.1 (E), Q1TTL2.1 (E), Q1TTL3.1 (E), QW1.1 (E), RP3.1
unnamed: QP1.2 (B), RP1.2, RP2.1
unnamed: 24V.2, C1.2 (-)
unnamed: 24TO5.1, QP1.3 (C), RP3.2
unnamed: 24TO5.2, RP1.1
unnamed: QW1.2 (B), RW1.2
unnamed: QW1.3 (C), RW2.1
unnamed: QW2.2 (B), RW2.2, RW3.1
unnamed: 5V_12V.1, QW2.1 (E), RW3.2
unnamed: DW1.1 (C), QW2.3 (C), WATER.1
unnamed: Q1TTL3.2 (B), R1TTL3.2
unnamed: Q1TTL3.3 (C), R2TTL3.1
unnamed: Q2TTL3.2 (B), R2TTL3.2, R3TTL3.1
unnamed: Q2TTL3.3 (C), TTL_3.1
unnamed: Q1TTL2.2 (B), R1TTL2.2
unnamed: Q1TTL2.3 (C), R2TTL2.1
unnamed: Q2TTL2.2 (B), R2TTL2.2, R3TTL2.1
unnamed: R1TTL3.1, TTL_3.2
unnamed: Q1TTL1.2 (B), R1TTL1.2
unnamed: Q1TTL1.3 (C), R2TTL1.1
unnamed: Q2TTL1.2 (B), R2TTL1.2, R3TTL1.1
unnamed: R1TTL2.1, TTL_2.2
unnamed: Q1TTL0.2 (B), R1TTL0.2
unnamed: Q1TTL0.3 (C), R2TTL0.1
unnamed: Q2TTL0.2 (B), R2TTL0.2, R3TTL0.1
unnamed: 24V.1, Q2TTL0.1 (E), Q2TTL1.1 (E), Q2TTL2.1 (E), Q2TTL3.1 (E), R3TTL0.2, R3TTL1.2, R3TTL2.2, R3TTL3.2
unnamed: Q2TTL2.3 (C), TTL_2.1
unnamed: R1TTL0.1, TTL_0.2
unnamed: Q2TTL0.3 (C), TTL_0.1
unnamed: R1TTL1.1, TTL_1.2
unnamed: Q2TTL1.3 (C), TTL_1.1
unnamed: RW1.1, WATER.2
unnamed: 5V_12V.2, QP1.1 (E), RP2.2

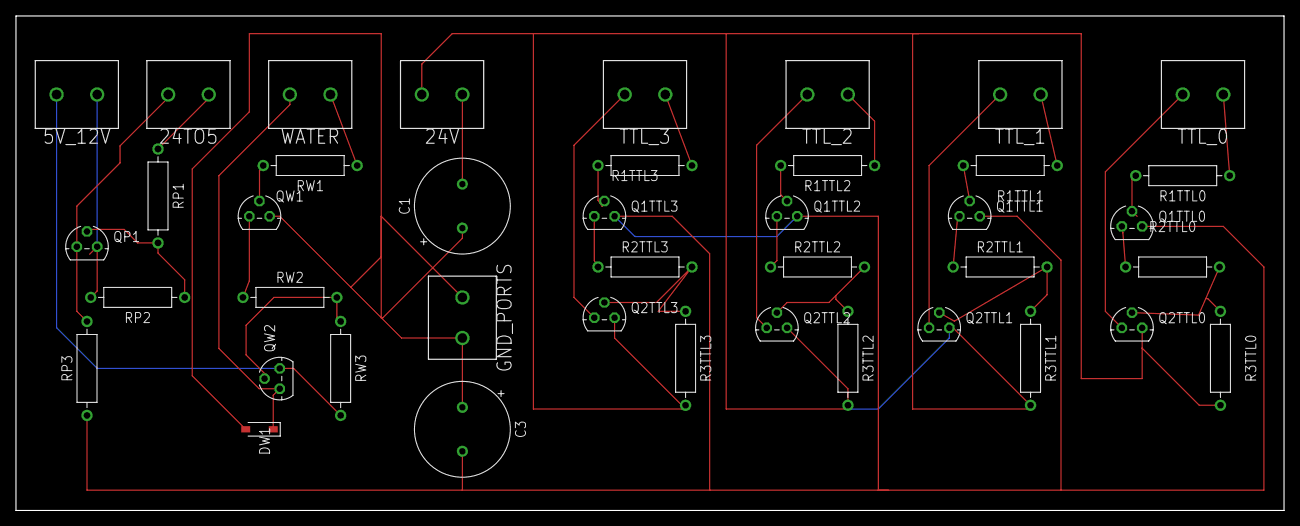
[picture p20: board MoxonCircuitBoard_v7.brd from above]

Board: 2 copper layers, 158.7 x 61.9 mm, 41 parts (0 on the bottom side), 33 nets.

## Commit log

2019-09-13 Add files via upload
    Tested Changes using Queue for images and update_idletasks, however some errors are happening, so this commit is mostly to save other functionality that has been added such as adjusting for the Discr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
2019-09-13 Add files via upload
    Both Updated and displaying images (disc stim and disc stim go) currently. Added in handling for Area1,2 left,right. brought both together for all necessary changes. Note: for Queue will need to chan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
2020-02-25 Add files via upload
    Changed order of some csv stuff and added in correct vs incorrect distinction. Added spots for event timestamps to go, have 5 currently, plus will need 8 for joystick directions
2020-02-27 Add files via upload
    Added Notes for where the PyDaqMx Event Timestamps should be. Will test on 2/27. Need to test task and task2. Commented out task3, not currently in use.
2020-02-28 Add files via upload
    Most Events going into csv. Small bug where sometimes the end of trial doesnt get added to csv, but it is currently saved in .plx file. Still working to figure out cause, seems random, but mostly it 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
2020-02-28 Add files via upload
    Added reset to Training with DS, STARTSTOP is functional and csv working with slight exceptions on Trial End times( these are correct in plexon .plx files), StartSTOP Events is currently testing wins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
2020-03-05 Add files via upload
    Working, checked Timestamps and End of Session CSV vars. Waiting on connector to have t start and t exit into plx as well. Need to check on update speed of the GUI.
2020-03-07 Add files via upload
    DS_GC: Changed format of CSV. Have just about everything except some things that require connector. Small Bug with Go Cue Stimuli.
    Need to bring most of the changes over to joystick program.
2020-03-09 Add files via upload
    Changed Reward Thread, Go cue now shows up on csv. had an error with reward thread blocking it? updated gathering_data_omni to change the try block. Need to look into loop timing of this again. Also 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
2020-03-10 Add files via upload
    Bugs / Fixed Today 3/10/2020:
    Fixed: Runtime Error in Saving CSV: Put whole function in try block.
    Also wrote DictToCSVWriter.py if needed for copying from word doc
    Fixed: Testing Timestamp Shift: 3/10/2020
    Take TS directly form the TTL pulse on Ch 9 and 10 for HandInTime and HandOutTime. *Important* This change requires that the new connector is used for the trial.
    If connector needs to be taken off for any reason refer to Github version on 3/09/2020 for 'working' change with small timstamp shift.
2020-03-11 Add files via upload
    Removed print statements and other unnecessary parts of gathering omni data.
2020-03-25 Add files via upload
    added in some error checking, need to work on a print traceback of errors
2020-06-02 Begin debugging of MonkeyImages_Joystick_Test.py--the version to read in task parameters from a config file on start-up. Though it appears to be reading in and assigning the values correctly; it is N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
    [csvconfig.csv, csvconfig_20200515.csv]
2020-06-15 Added a new case to *_Joystick_Conf.py: TaskType == HomezoneExit, that rewards the monkey for moving his hand out of homezone after appearance of the go cue. Monkey must move his hand out prior to en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
2020-06-17 Minor change made to filename assembly: the string contained in self.TaskType is now appended, rather than 'Joystick' only. '
2020-07-30 Re-organization of repo directory. Development iterations of code placed in 'development' directory.
    [csvconfig.csv, csvconfig_20200515.csv]
2020-08-04 Major updates to NHP_IntervalTimingTaskDetail.md to describe importing parameters from configuration file.
    [Output_EXAMPLE_HomezoneExit.csv, Output_EXAMPLE_Joystick.csv, csvconfig_EXAMPLE_HomezoneExit.csv, csvconfig_EXAMPLE_Joystick.csv]
2020-09-29 add mock and sham modes, add motor control abstraction
2020-10-01 fix motor control
2021-01-12 joystick: new event loop
    [csvconfig_EXAMPLE_Joystick.csv]
2021-04-30 joystick: update documentation
    [csvconfig_EXAMPLE_Joystick.csv]
2021-04-30 joystick: fixes, add log csv
    [csvconfig_EXAMPLE_Joystick.csv]
2021-05-14 joystick: remove unused config values, add water on/off UI buttons, update example config and docs, reduce saturation of images, change when sounds are played, re-add Time Out config, add reward dura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
    [csvconfig_EXAMPLE_Joystick.csv]
2021-07-10 joystick: update for new hardware wiring, improve error messages
2021-07-18 joystick: allow live view to fall behind actual data without failing, add calibrated live view, add live view downsampling, update readme
2021-08-24 add touchscreen programs
    [55mm x 45mm Cover v2.step, Arm Block.dxf, Arm Blocker.step, Bottom Cuff v3.step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]
2021-08-25 tilt: add documentation
    [MoxonCircuitBoard_v7.brd, MoxonCircuitBoard_v7.sch]
2021-09-13 joystick: add joystick_channel and post_succesful_pull_delay config values
    [csvconfig_EXAMPLE_Joystick.csv]
2021-09-25 joystick: delete old files
    [Output_EXAMPLE_HomezoneExit.csv, Output_EXAMPLE_Joystick.csv]
2021-09-25 tilt: add psth test main, adjust sample batch size, update gitignore
2021-09-25 joystick: update requirements, update example readme
    [csvconfig_EXAMPLE_Joystick.csv]
2021-11-03 tilt: update device number for motor control
2021-11-04 tilt: add comments about interactions with motor controller
2021-12-17 re-organize tilt code/docs
    [MoxonCircuitBoard_v7.brd, MoxonCircuitBoard_v7.sch]
2022-01-26 joystick: add image_ratios config value
    [csvconfig_EXAMPLE_Joystick.csv]
2022-03-17 tilt: add wiring docs
2022-03-18 tilt: add downsampling board to wiring docs
2022-04-07 new motor controller script
2022-04-27 touch: improve error message when correct plexon device isn't found
2022-07-15 update motor controller scripts
2022-09-22 tilt: fix digital signal recording, rewrite motor control to use serial
2022-09-23 tilt: fix motor initialization, fix stim
2022-12-20 tilt: update for gearbox and new sensor ports
2023-02-13 touchscreen: initial game flow logic refactor, add nidaq output
2023-02-13 tilt: add motor position tracking (disabled), add random classifier, add classifier config setting
2023-07-06 joystick: restructure as package
    [csvconfig_EXAMPLE_HomezoneExit.csv, csvconfig_EXAMPLE_Joystick.csv]
2023-10-10 touch: rewrite touchscreen game
    [55mm x 45mm Cover v2.step, Arm Block.dxf, Arm Blocker.step, Bottom Cuff v3.step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]
2023-11-13 joystick: real online classification
    [csvconfig_EXAMPLE_Joystick.csv]
2023-12-03 touch: add fake fullscreen, update readme, use butil plexdo, allow nidaq device selection
2024-02-01 joystick: process all analog samples coming from plexon
2024-02-01 tilt: incomplete update of wiring documentation
